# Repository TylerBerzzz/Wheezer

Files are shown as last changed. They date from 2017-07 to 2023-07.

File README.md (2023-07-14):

# The Wheezer

<p align="center">
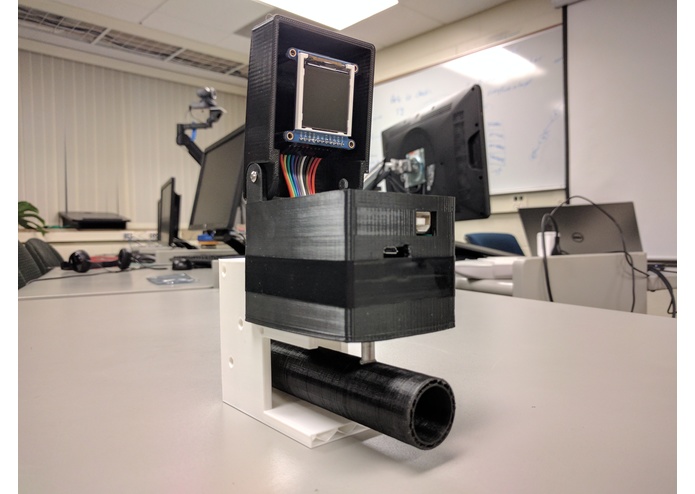
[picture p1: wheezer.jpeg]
  
</p>

Intel Hackathon 2017

Project Link: https://devpost.com/software/wheezer-418n3w

# What is it?
Our device measures the exhalation flow rate via the pressure drop through a venturi. Based on the venturi dimensions, the fluid density, and the pressure drop, the flow rate can be calculated and integrated for the total lung capacity. This information is plotted on a digital display on the device and is also transmitted via bluetooth to a connected android device.

# Inspiration
Asthma affects approximately 1 in 12 people in the US (AAAAI, 2001). The most significant measurement for quantifying asthma severity is the pulmonary lung function test. One such function test includes spirometry, which is used to assess the lung volume and exhalation rate of the patient. Without health insurance, these tests can cost over $200 per visit (Healthcare Bluebook). Our goal is to design a low-cost device for spirometry testing that can accurately assess the patients lung capacity and flow rate during exhalation.

# Circuit Information
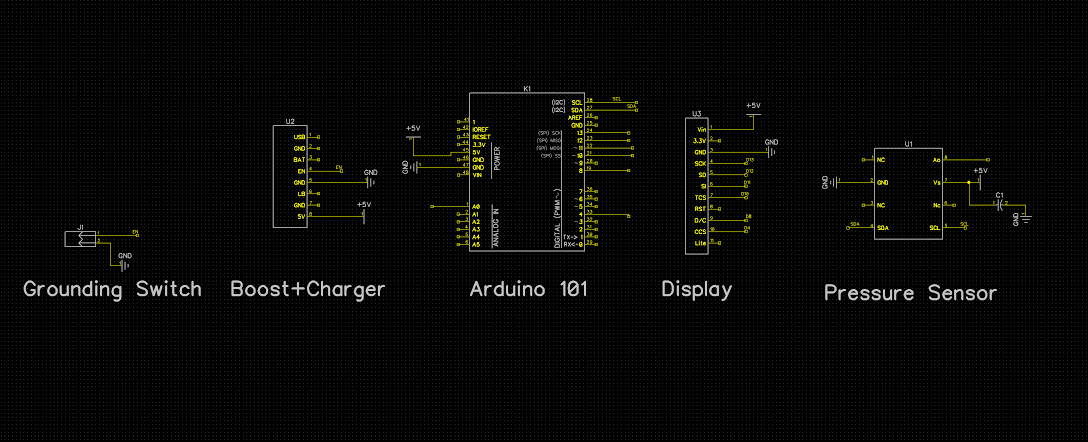
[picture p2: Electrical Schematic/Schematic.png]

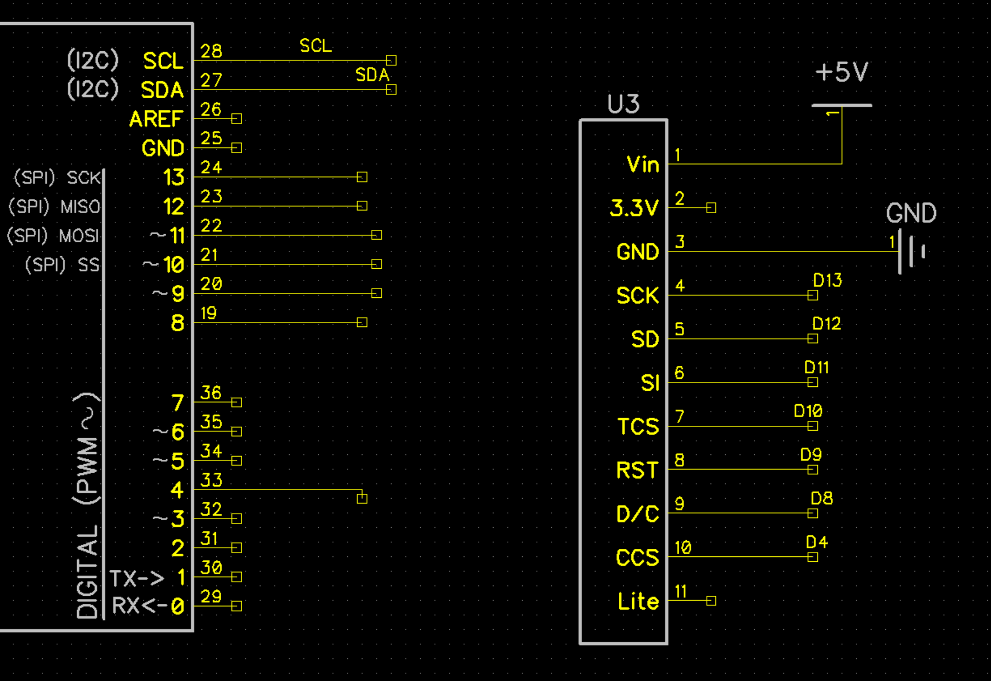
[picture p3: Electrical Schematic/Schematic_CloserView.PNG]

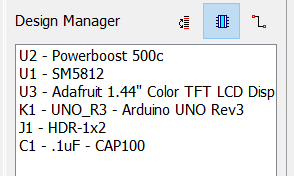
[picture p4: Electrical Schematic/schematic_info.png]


This image is a snapshot of a schematic in DIPTRACE. DIPTRACE is a freeware program used for circuitry design. The schematic file is inside the Electrical Schematic folder.

To avoid the lower resolution of the Arduino 101*, we needed to use a differential pressure sensor with i2c communication. We chose to use the SM5812 because it was affordable and had the option to output data over i2c or its analog output. We wanted our device to be portable, so we chose a 3.7V 500 mAh battery from Adafruit. The SM5812 needs to have 5V, so we chose the Powerboost 500c charger in order to boost the battery voltage. The Powerboost 500c charger also has the capability to charge the battery, which is super aweosome. To turn on and off the device, there is a switch between EN and ground on the PowerBoost 500 charger. When we started the project, the 1.44" TFT LCD Display was going to perform the realtime graphing operations for the data; however, we ended up deciding to switch to performing the realtime operations on an Android device through Bluetooth (which kind of defeats the purpose of the LCD.) This switch allowed us to fully use the arduino 101's BLE. An important note on the LCD: If you want to control the Backlight, you'll need to hook the LITE pin up to a PWM pin on the Arduino 101. I chose not to, which can clearly be seen in the schematic. Also, to run the code with no errors, use a SD card with the intel.bmp image in it. The purchasing links are in the BOM section.

*The arduino 101 operating voltage is 3.3V, thus the analog input pins go from 0 to 3.3V. That cuts off everything over 3.3V that a 5V sensor would output. You can scale the a voltage output to fit the 3.3V cut off; however, we found that i2c was the simplest method that would require the least components.  

# Our PCB
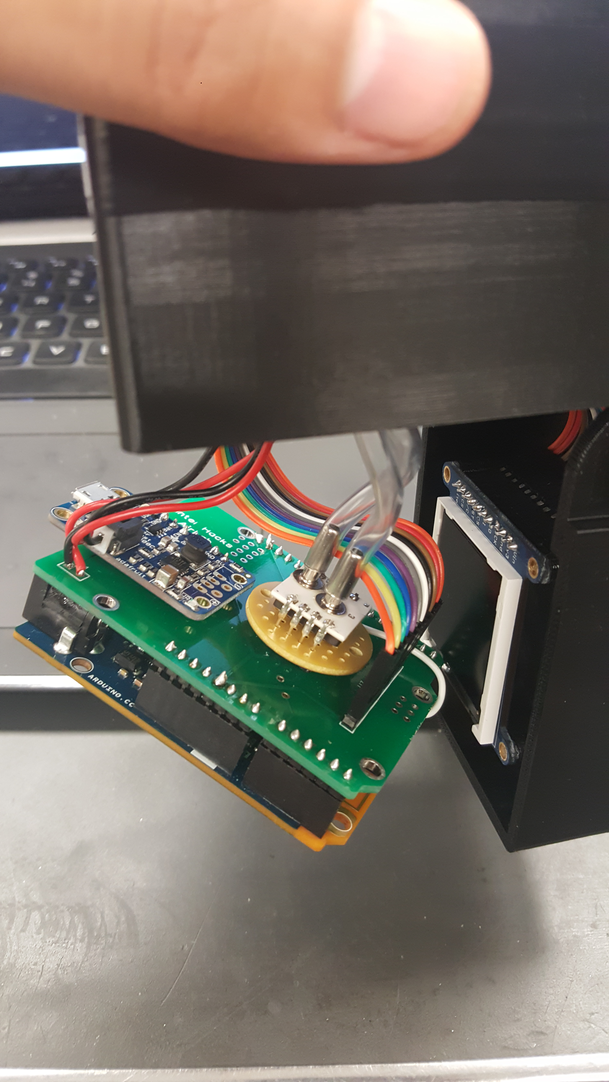
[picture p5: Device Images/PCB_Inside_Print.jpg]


We ordered our PCB from SEEEDStudio*. We were debating on whether or not to provide the routing and GERBER files on Github; we ended up deciding not to because the SM5812 has recently become an  NRND (Not recommended for new designs) component. 

SEEEDStudio: https://www.seeedstudio.com/fusion_pcb.html

# Data Comparison
In order to see how accurate #TheWheezer was, we needed to compare it to a medical grade instrument. Since Tyler has asthma, it was very easy to get the spirometry data. 

## Data gathered at the doctors office:
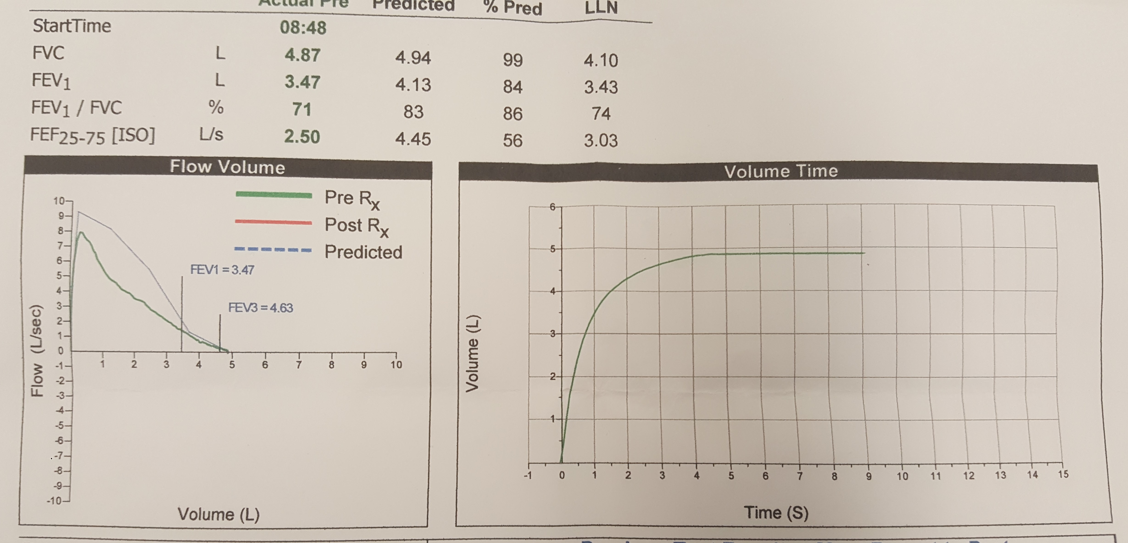
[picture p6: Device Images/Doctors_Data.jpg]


+ FVC = ~8

+ Peak = 4.87

+ FEV1 = 3.47

### Important Takeaways

+ The peak in the left graph represents how well air is moving through your airways at the time you take the test. Typically asthmatics have something called a "peak flow meter" which only measure the fastest flow you expel. It can be a helpful monitor for measuring present asthma symptoms; however, the peak doesn't tell you anything about your small airways- which makes these available devices limited.

+ FVC stands for forced vital capacity. FVC is the total amount of air exhaled during the test.

+ FEV stands for Forced expiratory volume, which measures how much air you can exhale during a forced breath. 

+ FEV1 - The amount of air exhaled may be measured during the first second

## Our Data:
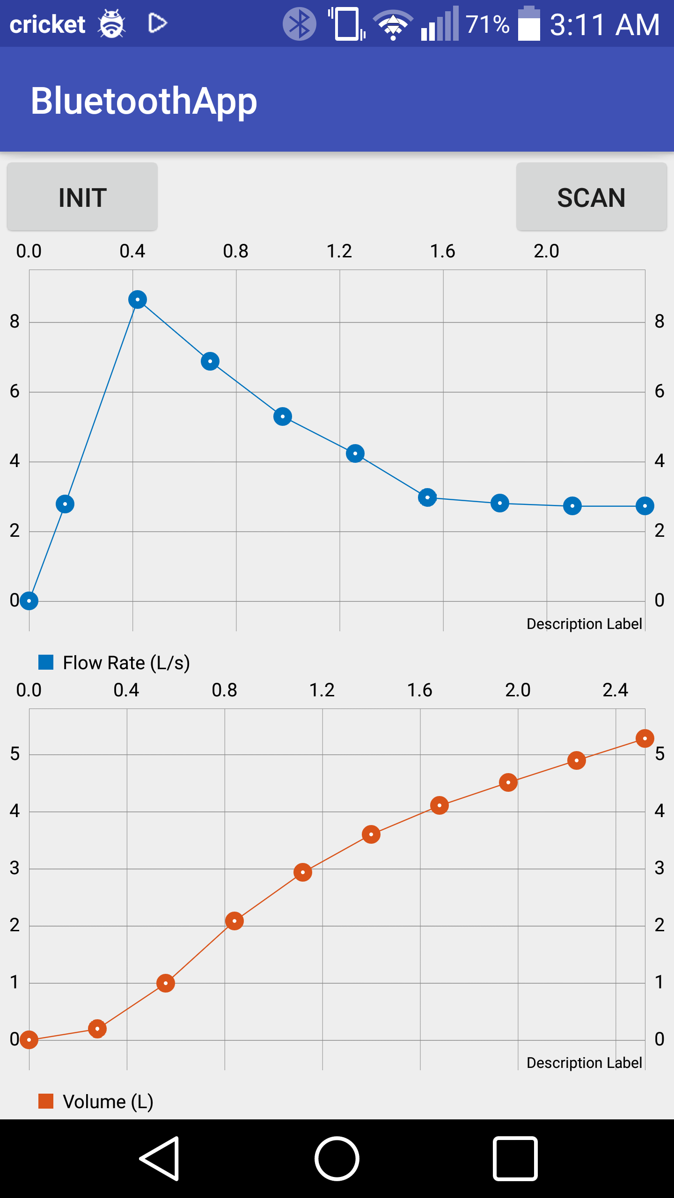
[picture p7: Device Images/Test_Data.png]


+ FVC = 8.2

+ Peak = 5.1

+ FEV1 = ~2.6

### Important Takeaways

+ Note that the Volume vs Time graph is created by integrating the Flow Rate vs Time Data. 

+ The blue line on the Flow Rate vs Time graph drops off at 2.74 L/s because it is the threshold that #TheWheezer is set to. The threshold is relatively high because the Differential pressure sensor is not sensitive enough to measure very low pressure drops. It ends on 2.74V and not 0 because the arduino code exits the plotting loop when the sensor is below the threshold. We expected the threshold to be lower. 

# Conclusion
+ Our graph compares nicely with the Doctors graph. Our results are not identical because we do not have a medically accurate instrument with required margins of error; however, the results correlate very well!

# Future Improvements?
It is possible that future iterations of Wheezer could also include a parallel measurement using a hot-wire anemometer to cover the low flow range while the venturi covers the upper range. Future iterations of Wheezer will also be able to save the patients data to their phone to track lung strengthening or deterioration over time. The instrument will also be redesigned for greater portability and convenience in maintenance.

# Datasheets
SM5812: http://www.mouser.com/ds/2/589/SM5812-254991.pdf

# BOM (Build of Materials)
+ ($14.95) Adafruit 1.44" Color TFT LCD Display with MicroSD Card breakout: https://www.adafruit.com/product/2088#tutorials
+ ($14.95) PowerBoost 500 Basic - 5V USB Boost @ 500mA from 1.8V+: https://www.adafruit.com/product/1944
+ ($7.95) Lithium Ion Polymer Battery - 3.7v 500mAh: https://www.adafruit.com/product/1578#tutorials
+ Switch: We just found a SPDT switch lying around somewhere
+ ($39.95) Arduino 101 Curie: https://www.adafruit.com/product/3033
+ ($4.90 (without shipping)) PCB from SEEEDstudio
+ ($17.35) Pressure Sensor: http://www.mouser.com/ProductDetail/Silicon-Microstructures-Inc/SM5812-005-A-3-LR/?qs=SaTeGCoDkn3W1sd7OhXrnA%3D%3D

### Total Price of everything: $100.05
### Price if you wanted to use power through the USB:  $77.15
### Price if you wanted to use power through the USB and didnt want the LCD: $62.20

### Medical Spirometers: https://www.medicaldevicedepot.com/Spirometers-s/30.htm

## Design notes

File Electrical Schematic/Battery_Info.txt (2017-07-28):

Battery is not included in the schematic:
3.7V Lithium Ion battery (500 mAh)

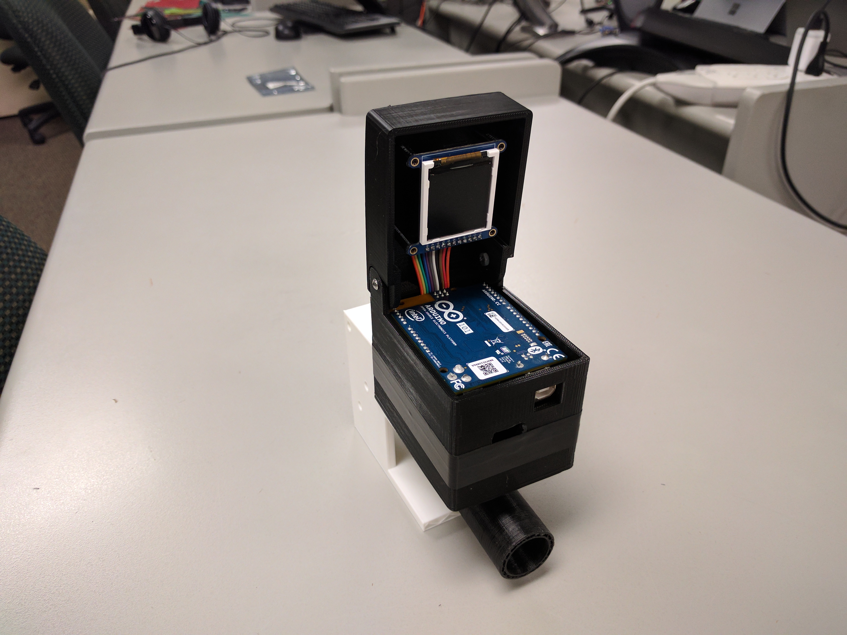
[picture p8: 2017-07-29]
Device Images/Pic2.jpg

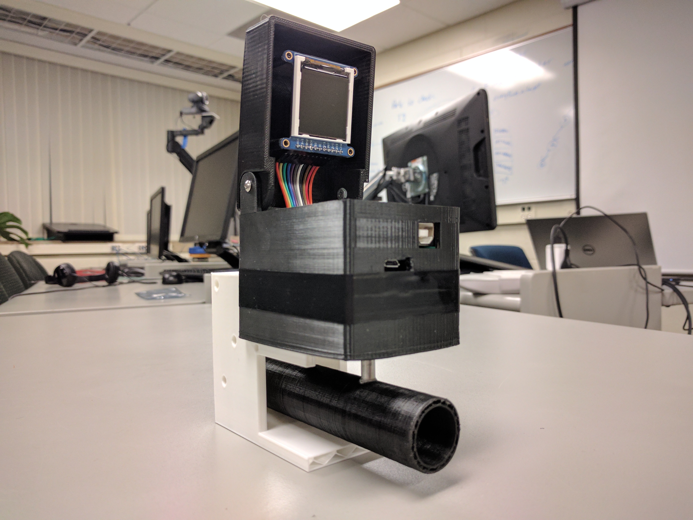
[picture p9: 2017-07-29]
Device Images/Pic1.jpg

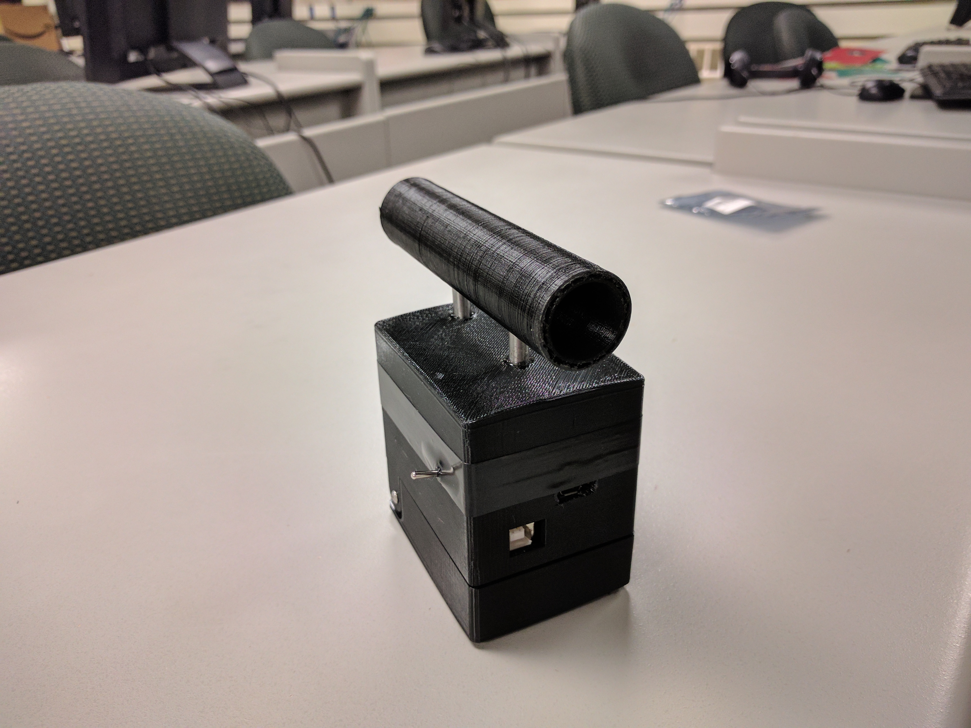
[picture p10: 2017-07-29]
Device Images/Pic3.jpg

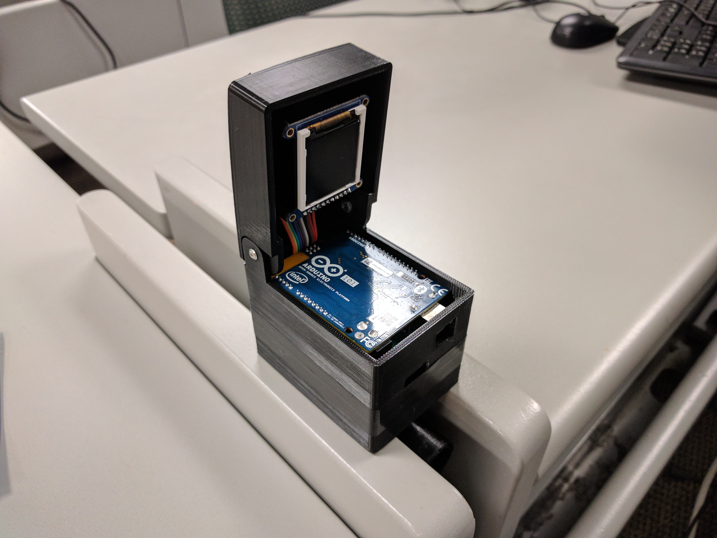
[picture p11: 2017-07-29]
Device Images/Pic4.jpg

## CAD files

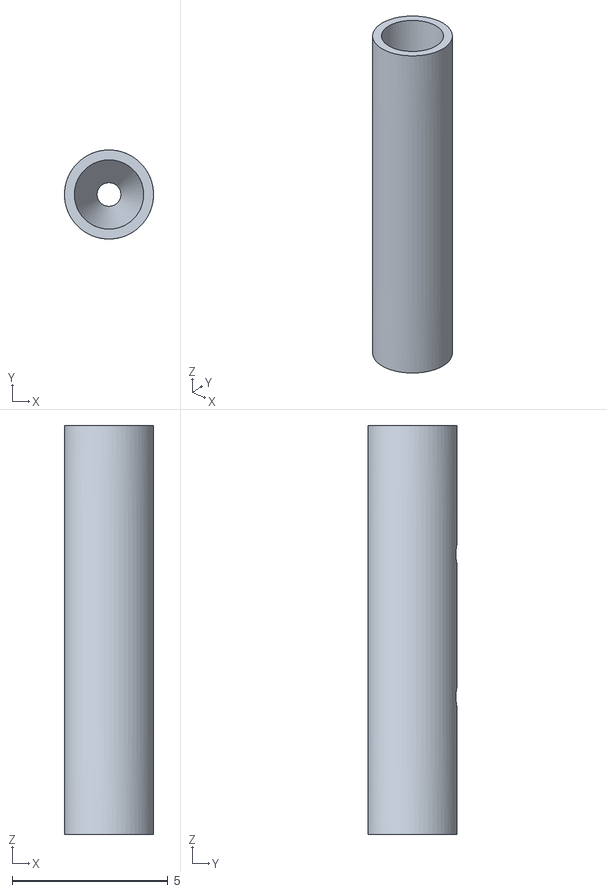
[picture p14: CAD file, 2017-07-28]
3D Prints/venturi_ver02.stl
2.86 x 2.86 x 13.1

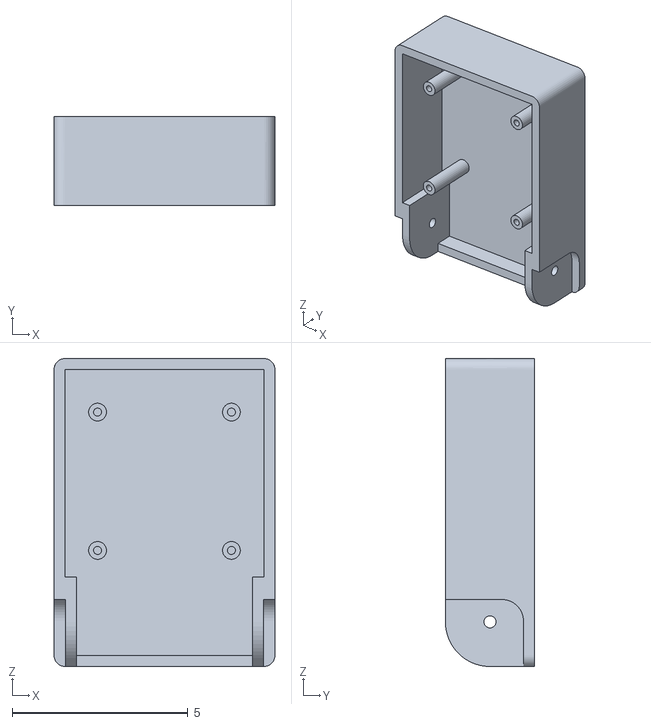
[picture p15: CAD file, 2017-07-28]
3D Prints/box_lid_ver01.stl
6.29 x 2.54 x 8.76

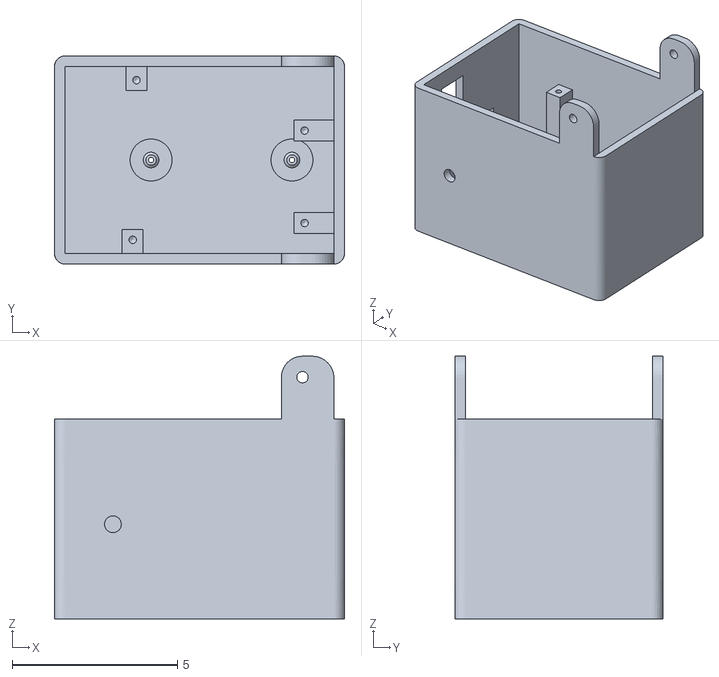
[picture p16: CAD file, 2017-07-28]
3D Prints/box_base_ver03.stl
8.76 x 6.29 x 7.94
